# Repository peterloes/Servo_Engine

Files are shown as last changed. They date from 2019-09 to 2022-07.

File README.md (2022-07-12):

# SERVO Engine

A standalone platform for animal manipulation. 

This is the firmware for project Servo_2015, a small board which allows to
control a servo via its PWM input. Setup and control of the servo is done
via 3 keys, and, for selecting the two end positions, also via two external
inputs, please see below. The firmware supports soft-start, i.e. the servo
speed will be ramped-up during the start phase.

Technical specifications:
- Input voltage: 12-42V
- Standby current consumption: 3mA@12V
- Maximum current consuption: 1.5A
- Dimensions: 60 × 50 × 10 mm

Supported:
- HiTEC HS-5646WP
- HiTEC HS 785(sailing winds)

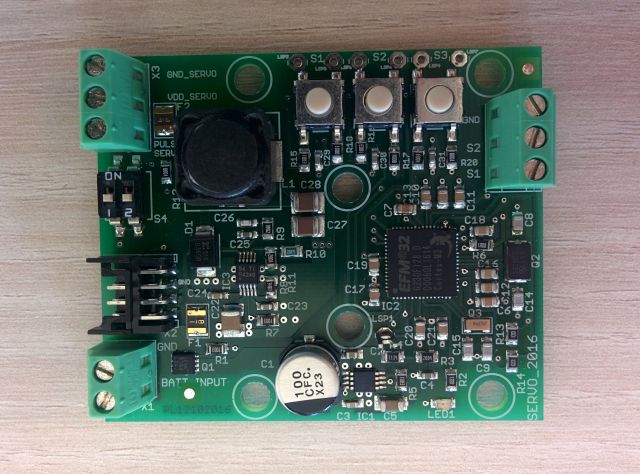
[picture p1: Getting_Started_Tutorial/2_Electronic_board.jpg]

 
 Setup Mode
 
 The servo setup procedure consists of 4 steps:
 - Adjust end position 1.  This can be the most left or the most right end
   point.  This position will be reached after power-up if valid servo data
   has been found in FLASH.
 - Adjust end position 2.  This is the opposite end position to position 1.
 - Adjust servo speed.  The servo permanently moves between the two end
   points.  The speed can be adjusted via S1 and S2.
 - Asserting S3 the 4th time stores the servo parameters into FLASH and
   returns to normal operation

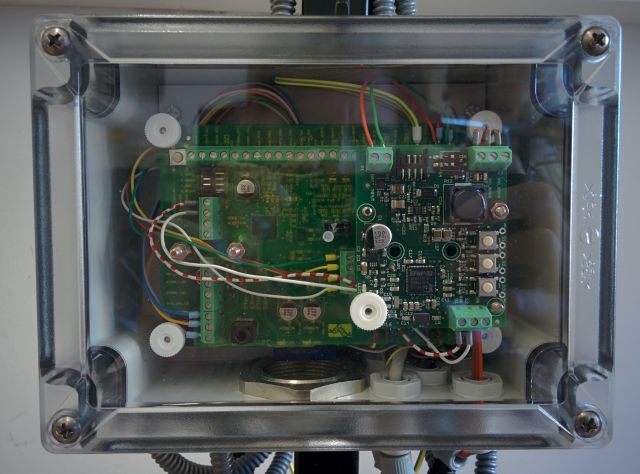
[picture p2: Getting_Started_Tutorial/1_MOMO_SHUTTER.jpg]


Bird Feeder Application (MOMO)

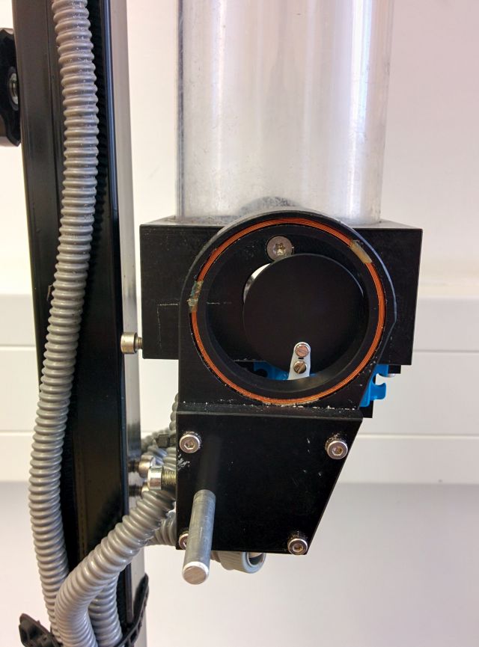
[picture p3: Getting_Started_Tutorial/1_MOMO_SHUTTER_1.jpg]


Bird Feeder Application

https://github.com/peterloes/Servo_Engine/blob/master/Getting_Started_Tutorial/1_poster_overview.pdf

Mainboard: 

https://github.com/peterloes/MOMO

https://github.com/peterloes/TAMDL

Manufacture:

https://github.com/peterloes/Servo_Engine/blob/master/Getting_Started_Tutorial/3_Supplier.txt

EXTENSIONS:

Electrical applications for non-deadly animal traps.

https://github.com/peterloes/SmartAnimalTraps

Antenna (horizontal) rotation over 360 degrees (HiTEC HS 785//sailing winds; 12V@25mA).

https://github.com/peterloes/Servo_Engine/blob/master/Getting_Started_Tutorial/2_Servo_Antenna_3turns.jpg (New firmware is not uploaded.)

Actuator for linear movements.

https://github.com/peterloes/Linear_Engine

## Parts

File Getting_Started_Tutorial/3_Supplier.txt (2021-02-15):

Supplier of all Electronic Boards

Top-Print Electronic GmbH
Oskar Schmid

Rosenheimer Landstr. 129a
85521 Ottobrunn
Germany
Tel.: +49-89-60668047
Fax: +49-89-60668049
mailto: info@top-print.eu
https://www.leiterplatten-muenchen.de/

Protective coating with Schmelzharz Bectron MR3404

KC – Kunststoff- Chemische Produkte GmbH
Holger Sarau-Burghardt

Leonberger Straße 86 
DE 71292 Friolzheim
phone: +49 (0)7044 9425 13
e-mail: h.sarau-burghardt@kc-produkte.com
http: www.conformalcoating.de

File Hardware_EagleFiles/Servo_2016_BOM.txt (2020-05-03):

Stückliste exportiert am 15.05.2018 12:53

Part  Value                Device                  Package                Description                                                    MF MPN OC_FARNELL OC_NEWARK
C1    100µ/16V             CPOL-EUE                PANASONIC_E            POLARIZED CAPACITOR, European symbol                                                      
C2    1uF                  C-EUC0603               C0603                  CAPACITOR, European symbol                                                                
C3    1nF                  C-EUC0603               C0603                  CAPACITOR, European symbol                                                                
C4    10nF                 C-EUC0603               C0603                  CAPACITOR, European symbol                                                                
C5    10uF                 C-EUC1206               C1206                  CAPACITOR, European symbol                                                                
C6    100n                 C_SMD0805               0805                                                                                                             
C7    1u                   C_SMD0805               0805                                                                                                             
C8    12p                  C_SMD0805               0805                                                                                                             
C9    18p                  C_SMD0805               0805                                                                                                             
C10   100n                 C_SMD0805               0805                                                                                                             
C11   100n                 C_SMD0805               0805                                                                                                             
C12   100n                 C_SMD0805               0805                                                                                                             
C13   100n                 C_SMD0805               0805                                                                                                             
C14   12p                  C_SMD0805               0805                                                                                                             
C15   18p                  C_SMD0805               0805                                                                                                             
C16   100n                 C_SMD0805               0805                                                                                                             
C17   100n                 C_SMD0805               0805                                                                                                             
C18   100n                 C_SMD0805               0805                                                                                                             
C19   100n                 C_SMD0805               0805                                                                                                             
C20   100n                 C_SMD0805               0805                                                                                                             
C21   100n                 C_SMD0805               0805                                                                                                             
C22   4.7µF                C-EUC1210               C1210                  CAPACITOR, European symbol                                                                
C23   10nF                 C-EUC0603               C0603                  CAPACITOR, European symbol                                                                
C24   100nF                C-EUC0603               C0603                  CAPACITOR, European symbol                                                                
C25   4.3nF                C-EUC0603               C0603                  CAPACITOR, European symbol                                                                
C26   24pF                 C-EUC0603               C0603                  CAPACITOR, European symbol                                                                
C27   22µF                 C-EUC1210               C1210                  CAPACITOR, European symbol                                                                
C28   22µF                 C-EUC1210               C1210                  CAPACITOR, European symbol                                                                
C29   10n                  C-EUC0603               C0603                  CAPACITOR, European symbol                                                                
C30   10n                  C-EUC0603               C0603                  CAPACITOR, European symbol                                                                
C31   10n                  C-EUC0603               C0603                  CAPACITOR, European symbol                                                                
D1    B360B                SCHOTTKY-DIODESMD       SMB                    Schottky Diode                                                                            
F1    USMF150              PFUF                    PFUF_1210POLY                                                                                                    
F2    USMF110              PFUF                    PFUF_1210POLY                                                                                                    
IC1   TPS7A1601DGNT        TPS7A16                 DGN_S-PDSO-G8-EXP                                                                                                
IC2   EFM32G230F128        EFM32G230F128           QFN64                  EFM32G230F128 Gecko Microcontroller in 9mm x 9mm QFN64 package                            
IC3   TPS54240DGQR         TPS54240DGQR            S-PDSO-G10                                                                                                       
L1    PIS4728-220M-04      DR127                   DR127                  High Power Density, High Efficiency, Shielded Inductors                                   
LED1  SML-H12U8TT86        LEDCHIPLED_0805         CHIPLED_0805           LED                                                                                       
LSP1  (n.b.)LSP10          LSP10                   LSP10                  SOLDER PAD drill 1.0 mm, distributor Buerklin, 12H555                                     
LSP2  (n.b.)LSP10          LSP10                   LSP10                  SOLDER PAD drill 1.0 mm, distributor Buerklin, 12H555                                     
LSP3  (n.b.)LSP10          LSP10                   LSP10                  SOLDER PAD drill 1.0 mm, distributor Buerklin, 12H555                                     
LSP4  (n.b.)LSP10          LSP10                   LSP10                  SOLDER PAD drill 1.0 mm, distributor Buerklin, 12H555                                     
LSP5  (n.b.)LSP10          LSP10                   LSP10                  SOLDER PAD drill 1.0 mm, distributor Buerklin, 12H555                                     
LSP6  (n.b.)LSP10          LSP10                   LSP10                  SOLDER PAD drill 1.0 mm, distributor Buerklin, 12H555                                     
LSP7  (n.b.)LSP10          LSP10                   LSP10                  SOLDER PAD drill 1.0 mm, distributor Buerklin, 12H555                                     
PASS1 ROUND_1MM1.5         ROUND_1MM1.5            ROUND2_1.5MM                                                                                                     
PASS2 ROUND_1MM1.5         ROUND_1MM1.5            ROUND2_1.5MM                                                                                                     
Q1    SI7121DN             TRANSISTOR-FET_SI7113DN TRANSISTOR-FET_1212-8S                                                                                           
Q2    NX5032GA/32MHz/8pF   CRYSTAL2P5.0X3.2        CRYSTAL2P5.0X3.2       Quarz Crystal                                                                             
Q3    CM7V, 32768Hz/12.5pF CRYSTAL2P               CRYSTAL2P3.2X1.5       Quarz Crystal                                                                             
R1    100k                 R-EU_R0805              R0805                  RESISTOR, European symbol                                                                 
R2    1K2                  R-EU_R0805              R0805                  RESISTOR, European symbol                                                                 
R3    2M                   R-EU_R0805              R0805                  RESISTOR, European symbol                                                                 
R4    1M13                 R-EU_R0805              R0805                  RESISTOR, European symbol                                                                 
R5    100K                 R-EU_R0805              R0805                  RESISTOR, European symbol                                                                 
R6    1                    R-EU_R0805              R0805                  RESISTOR, European symbol                                                                 
R7    100K                 R-EU_R0805              R0805                  RESISTOR, European symbol                                                                 
R8    348K                 R-EU_R0805              R0805                  RESISTOR, European symbol                                                                 
R9    39K                  R-EU_R0805              R0805                  RESISTOR, European symbol                                                                 
R10   53K                  R-EU_R0805              R0805                  RESISTOR, European symbol                                                                 
R11   10k                  R-EU_R0805              R0805                  RESISTOR, European symbol                                                                 
R12   100                  R-EU_R0805              R0805                  RESISTOR, European symbol                                                                 
R13   1K                   R-EU_R0805              R0805                  RESISTOR, European symbol                                                                 
R14   1K                   R-EU_R0805              R0805                  RESISTOR, European symbol                                                                 
R15   100K                 R-EU_R0805              R0805                  RESISTOR, European symbol                                                                 
R16   100K                 R-EU_R0805              R0805                  RESISTOR, European symbol                                                                 
R17   100K                 R-EU_R0805              R0805                  RESISTOR, European symbol                                                                 
R18   100                  R-EU_R0805              R0805                  RESISTOR, European symbol                                                                 
R19   100                  R-EU_R0805              R0805                  RESISTOR, European symbol                                                                 
R20   100                  R-EU_R0805              R0805                  RESISTOR, European symbol                                                                 
S1    SWPB_B3S1000         DTSM-6                  DTSM-6                                                                                                           
S2    SWPB_B3S1000         DTSM-6                  DTSM-6                                                                                                           
S3    SWPB_B3S1000         DTSM-6                  DTSM-6                                                                                                           
S4    SBS9102TK            219-02                  CTS-219-02             Surface Mount DIP Switch Series 219 SMT                               unknown    unknown  
X1    MKDS1/2-3,81         MKDS1/2-3,81            2POL381                MKDS 1/2-3,81 - Order No. 1727010 (RS-Online - 101-5384)                                  
X2    DP11_8DP_2DS         DP11_8DP_2DS            DP11_8DP-2DS                                                                                                     
X3    MKDS1/3-3,81         MKDS1/3-3,81            3POL381                MKDS 1/3-3,81 - Order No. 1727023 (RS-Online - 101-5390)                                  
X4    MKDS1/3-3,81         MKDS1/3-3,81            3POL381                MKDS 1/3-3,81 - Order No. 1727023 (RS-Online - 101-5390)

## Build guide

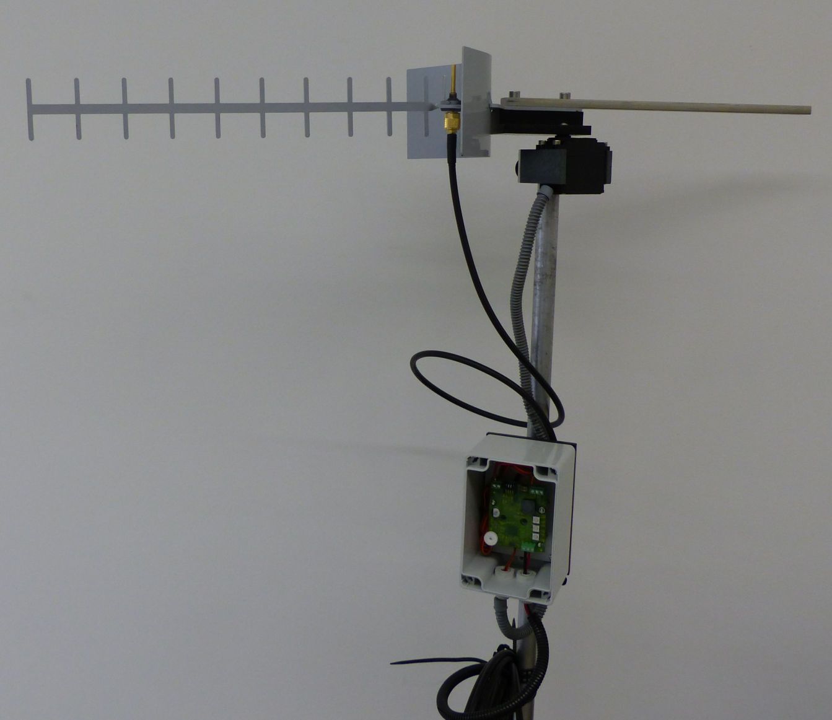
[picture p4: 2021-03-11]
Getting_Started_Tutorial/4_Servo_Antenna_3turns.JPG

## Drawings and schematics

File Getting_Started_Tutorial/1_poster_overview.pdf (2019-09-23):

## Multifunctional Mainboard to Observe and Manipulate Organisms (MOMO) RFID Readers and SERVO Engines

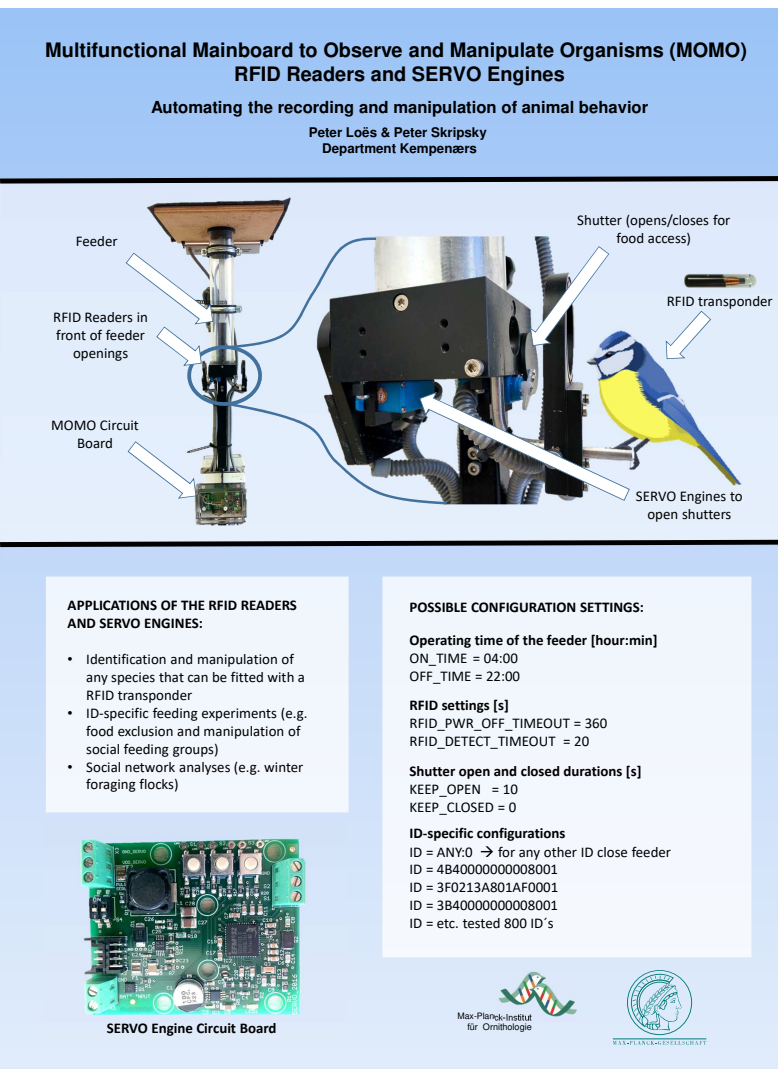
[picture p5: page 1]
APPLICATIONS OF THE RFID READERS; POSSIBLE CONFIGURATION SETTINGS:; Feeder; RFID transponder; RFID settings [s] RFID_PWR_OFF_TIMEOUT = 360 RFID_DETECT_TIMEOUT = 20; MOMO Circuit Board

Automating the recording and manipulation of animal behavior

Peter Loës & Peter Skripsky
Department Kempenærs

Shutter (opens/closes for
food access)

RFID Readers in
front of feeder
openings

SERVO Engines to
open shutters

AND SERVO ENGINES:

Operating time of the feeder [hour:min]
ON_TIME = 04:00
OFF_TIME = 22:00

• Identification and manipulation of
any species that can be fitted with a
RFID transponder
• ID-specific feeding experiments (e.g.
food exclusion and manipulation of
social feeding groups)
• Social network analyses (e.g. winter
foraging flocks)

Shutter open and closed durations [s]
KEEP_OPEN = 10
KEEP_CLOSED = 0

ID-specific configurations
ID = ANY:0 → for any other ID close feeder
ID = etc. tested 800 ID´s

Max-Planck-Institut
für Ornithologie

SERVO Engine Circuit Board

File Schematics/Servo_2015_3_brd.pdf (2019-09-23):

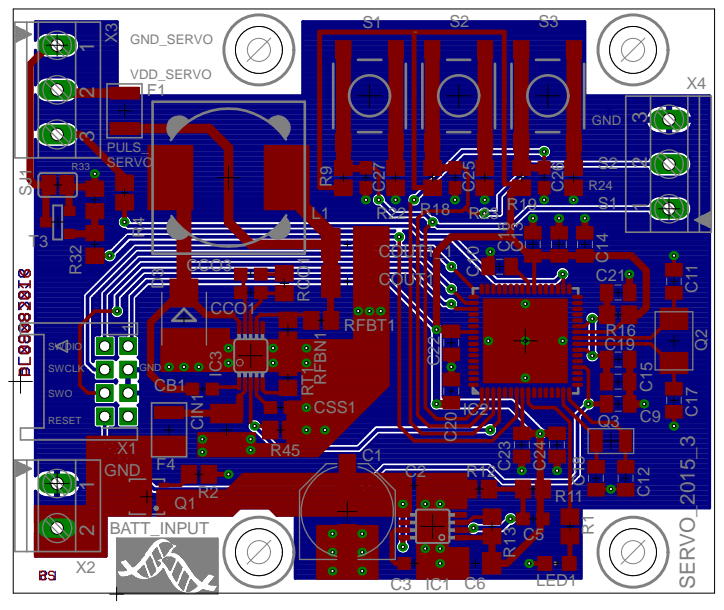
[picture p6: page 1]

SERVO | S2

RFBT1

R16
C19

SWDIO

SWO

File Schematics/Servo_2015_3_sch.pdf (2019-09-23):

## Wide Input Voltage Range: 12V to 42V VDD_SERVO 5V benötigt max. VIN 8V

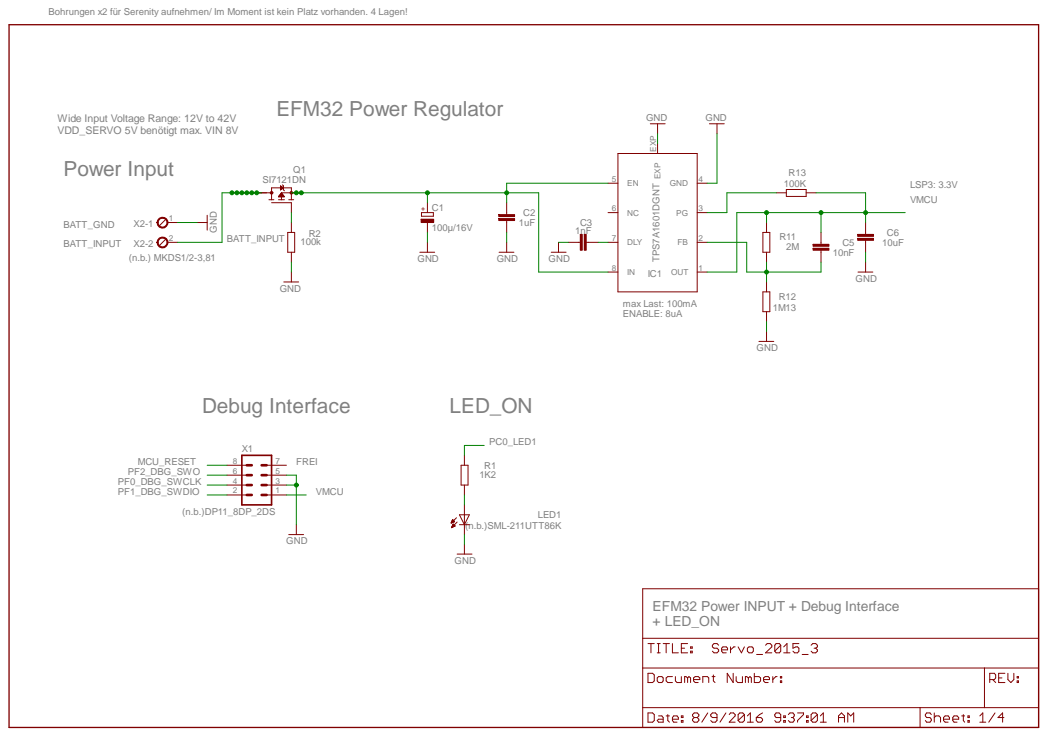
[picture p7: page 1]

Bohrungen x2 für Serenity aufnehmen/ Im Moment ist kein Platz vorhanden. 4 Lagen!

EFM32 Power INPUT + Debug Interface
+ LED_ON

# EFM32 I/O + POWER

# CL f. 32KHz crystal = 22pF as in STK3600

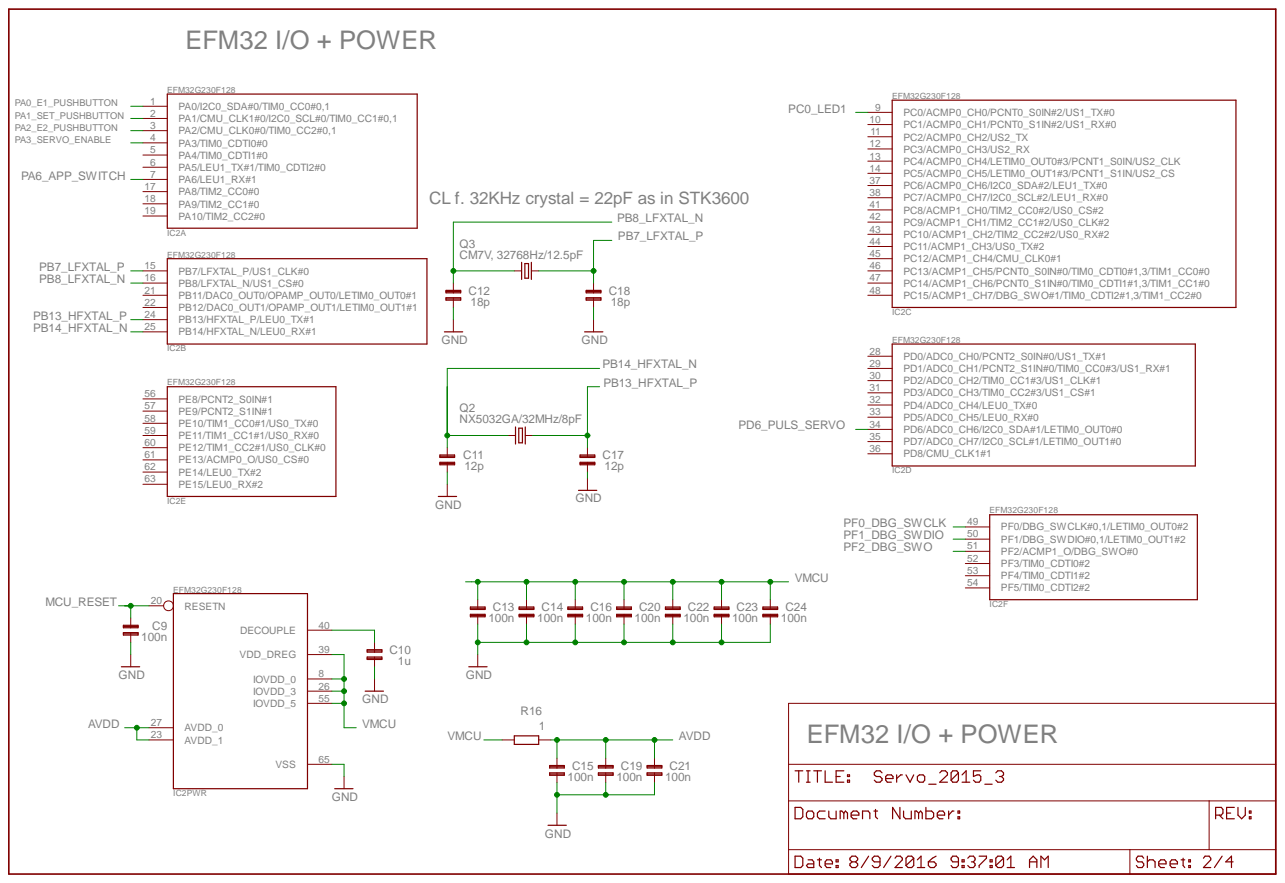
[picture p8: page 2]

# 5V_Ausgabe

# POWER OUTPUTs

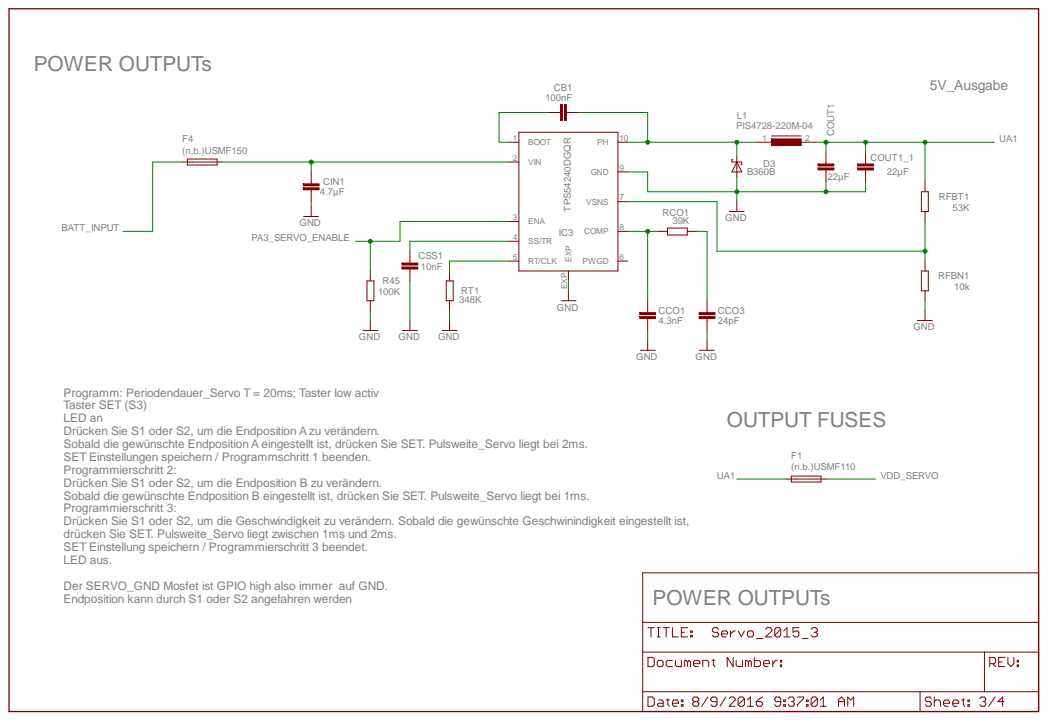
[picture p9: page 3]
POWER OUTPUTs; OUTPUT FUSES; GND; TPS54240DGQR; PIS4728-220M-04; (n.b.)USMF150; (n.b.)USMF110; CCO3; CSS1; RCO1; CIN1; VIN 2; ENA 3; VSNS; BOOT 1; COMP; RT/CLK 5; EXP EXP; PWGD; CCO1; RFBT1; RFBN1; COUT1; COUT1_1; VDD_SERVO; PA3_SERVO_ENABLE; BATT_INPUT

Programm: Periodendauer_Servo T = 20ms; Taster low activ
Taster SET (S3)
LED an
Drücken Sie S1 oder S2, um die Endposition A zu verändern.
Sobald die gewünschte Endposition A eingestellt ist, drücken Sie SET. Pulsweite_Servo liegt bei 2ms.
SET Einstellungen speichern / Programmschritt 1 beenden.
Programmierschritt 2:
Drücken Sie S1 oder S2, um die Endposition B zu verändern.
Sobald die gewünschte Endposition B eingestellt ist, drücken Sie SET. Pulsweite_Servo liegt bei 1ms.
Programmierschritt 3:
Drücken Sie S1 oder S2, um die Geschwindigkeit zu verändern. Sobald die gewünschte Geschwinindigkeit eingestellt ist,
drücken Sie SET. Pulsweite_Servo liegt zwischen 1ms und 2ms.
SET Einstellung speichern / Programmierschritt 3 beendet.
LED aus.

Der SERVO_GND Mosfet ist GPIO high also immer auf GND.
Endposition kann durch S1 oder S2 angefahren werden

# SERVO

## HITEC, C131_Graupner:

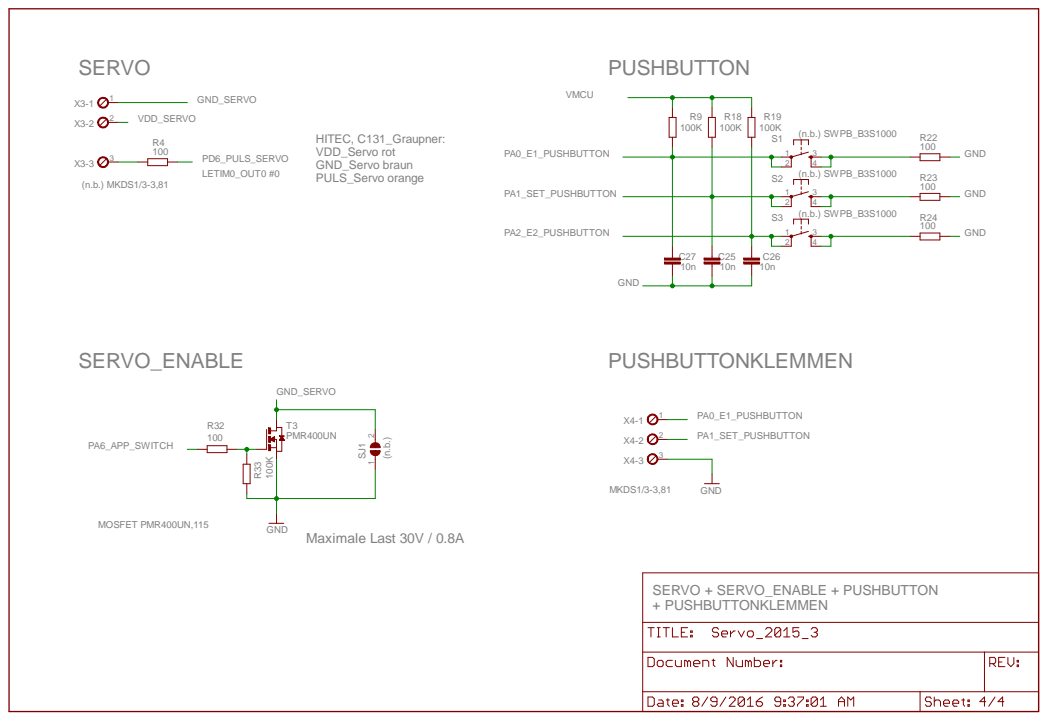
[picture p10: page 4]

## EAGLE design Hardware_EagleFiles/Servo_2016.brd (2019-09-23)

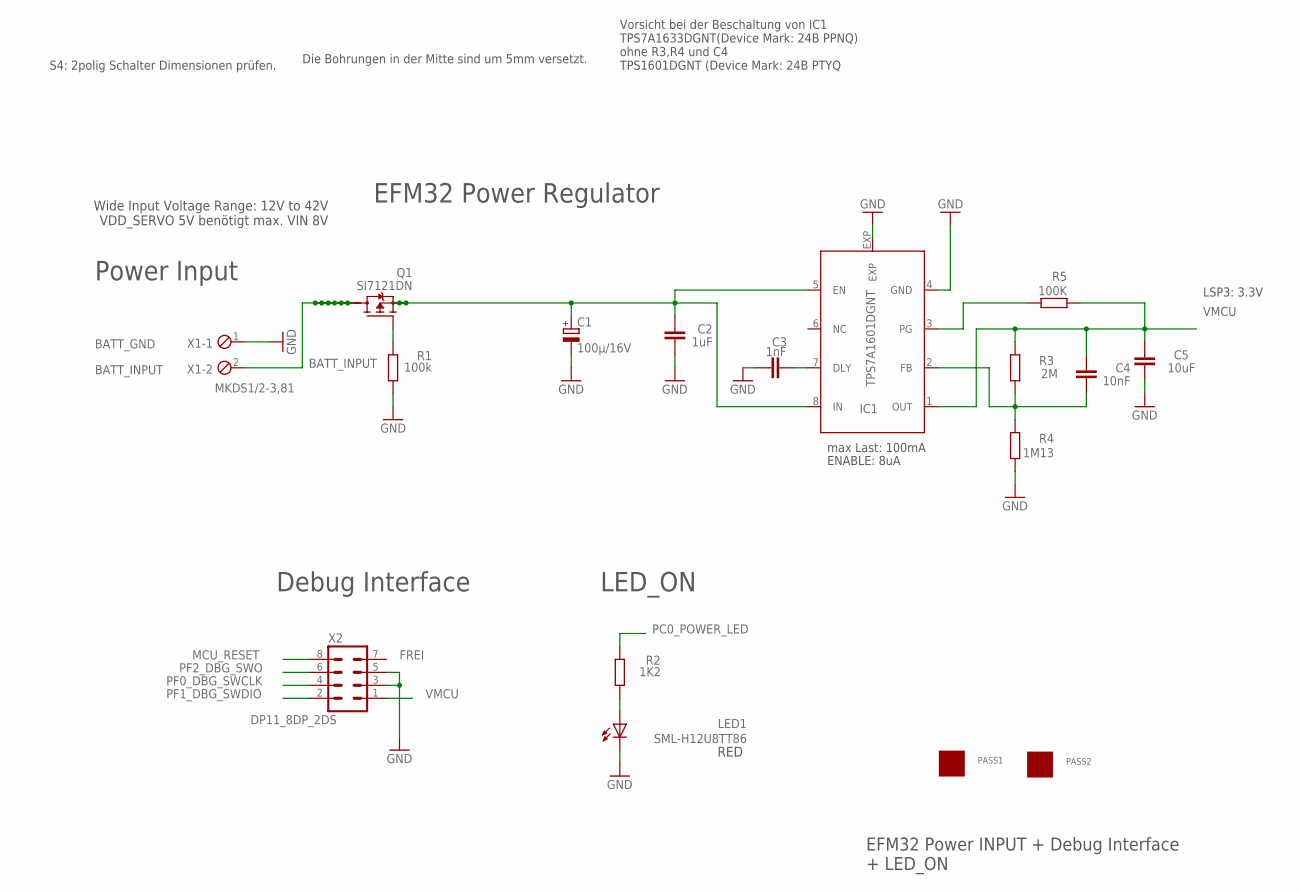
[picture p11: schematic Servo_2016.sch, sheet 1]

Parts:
C1: 100µ/16V; PANASONIC_E
C2: 1uF; C0603
C3: 1nF; C0603
C4: 10nF; C0603
C5: 10uF; C1206
IC1: TPS7A1601DGNT; DGN_S-PDSO-G8-EXP
LED1: SML-H12U8TT86; CHIPLED_0805
PASS1, PASS2: ROUND_1MM1.5; ROUND2_1.5MM
Q1: SI7121DN; TRANSISTOR-FET_1212-8S
R1: 100k; R0805
R2: 1K2; R0805
R3: 2M; R0805
R4: 1M13; R0805
R5: 100K; R0805
X1: MKDS1/2-3,81; 2POL381
X2: DP11_8DP_2DS; DP11_8DP-2DS

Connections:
BATT_INPUT: Q1.5 (D), Q1.6 (D), Q1.7 (D), Q1.8 (D), Q1.9 (D), Q1.10 (D), Q1.11 (D), X1.2; also elsewhere on the board
GND: C1.-, C2.1, C3.1, C5.1, IC1.4 (GND), IC1.EXP, LED1.C, R1.1, R4.1, X1.1, X2.3, X2.5; also elsewhere on the board
MCU_RESET: X2.8; also elsewhere on the board
unnamed: C1.+, C2.2, IC1.5 (EN), IC1.8 (IN), Q1.1 (S), Q1.2 (S), Q1.3 (S)
unnamed: C3.2, IC1.7 (DLY)
unnamed: C4.1, IC1.2 (FB), R3.1, R4.2
unnamed: IC1.3 (PG), R5.2
unnamed: Q1.4 (G), R1.2
unnamed: LED1.A, R2.2
PC0_POWER_LED: R2.1; also elsewhere on the board
PF0_DBG_SWCLK: X2.4; also elsewhere on the board
PF1_DBG_SWDIO: X2.2; also elsewhere on the board
PF2_DBG_SWO: X2.6; also elsewhere on the board
VMCU: C4.2, C5.2, IC1.1 (OUT), R3.2, R5.1, X2.1; also elsewhere on the board

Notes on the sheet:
BATT_GND
Wide Input Voltage Range: 12V to 42V VDD_SERVO 5V benötigt max. VIN 8V
BATT_INPUT
EFM32 Power INPUT + Debug Interface + LED_ON
ENABLE: 8uA
Power Input
max Last: 100mA
LSP3: 3.3V
EFM32 Power Regulator
Debug Interface
LED_ON
FREI
Vorsicht bei der Beschaltung von IC1 TPS7A1633DGNT(Device Mark: 24B PPNQ) ohne R3,R4 und C4 TPS1601DGNT (Device Mark: 24B PTYQ
S4: 2polig Schalter Dimensionen prüfen.
Die Bohrungen in der Mitte sind um 5mm versetzt.
RED

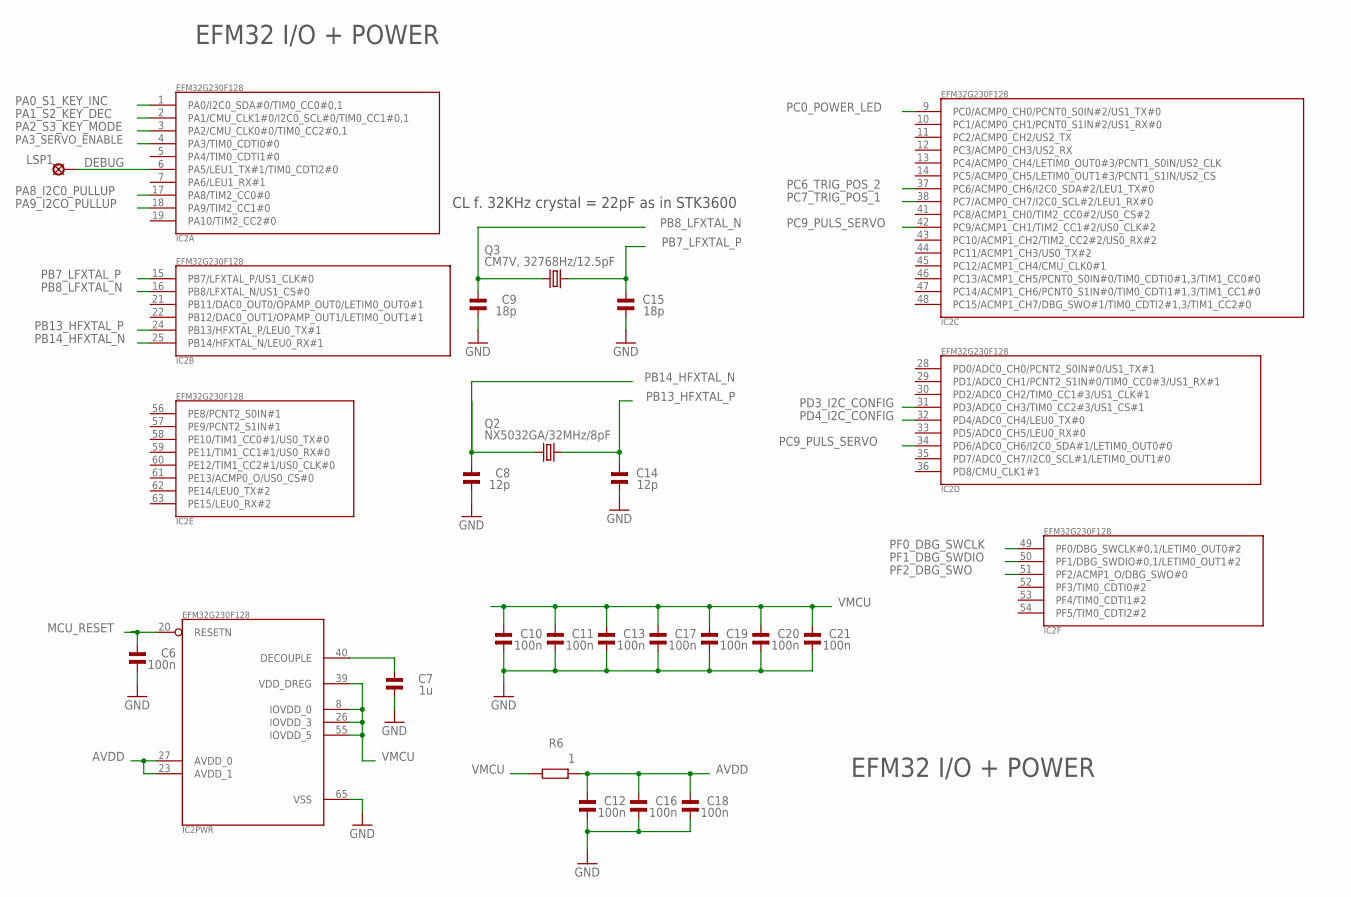
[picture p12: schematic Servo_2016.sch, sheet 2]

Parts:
C6, C10, C11, C12, C13, C16, C17, C18, C19, C20, C21: 100n; 0805
C7: 1u; 0805
C8, C14: 12p; 0805
C9, C15: 18p; 0805
IC2: EFM32G230F128; QFN64
LSP1: (n.b.)LSP10; LSP10
Q2: NX5032GA/32MHz/8pF; CRYSTAL2P5.0X3.2
Q3: CM7V, 32768Hz/12.5pF; CRYSTAL2P3.2X1.5
R6: 1; R0805

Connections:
AVDD: C12.2, C16.2, C18.2, IC2.23 (AVDD_1), IC2.27 (AVDD_0), R6.2
DEBUG: IC2.6 (PA5/LEU1_TX#1/TIM0_CDTI2#0), LSP1.MP
GND: C6.1, C7.1, C8.1, C9.1, C10.1, C11.1, C12.1, C13.1, C14.1, C15.1, C16.1, C17.1, C18.1, C19.1, C20.1, C21.1, IC2.65 (VSS); also elsewhere on the board
MCU_RESET: C6.2, IC2.20 (RESETN); also elsewhere on the board
unnamed: C7.2, IC2.40 (DECOUPLE)
PA0_S1_KEY_INC: IC2.1 (PA0/I2C0_SDA#0/TIM0_CC0#0,1); also elsewhere on the board
PA1_S2_KEY_DEC: IC2.2 (PA1/CMU_CLK1#0/I2C0_SCL#0/TIM0_CC1#0,1); also elsewhere on the board
PA2_S3_KEY_MODE: IC2.3 (PA2/CMU_CLK0#0/TIM0_CC2#0,1); also elsewhere on the board
PA3_SERVO_ENABLE: IC2.4 (PA3/TIM0_CDTI0#0); also elsewhere on the board
PA8_I2C0_PULLUP: IC2.17 (PA8/TIM2_CC0#0); also elsewhere on the board
PA9_I2CO_PULLUP: IC2.18 (PA9/TIM2_CC1#0); also elsewhere on the board
PB7_LFXTAL_P: C15.2, IC2.15 (PB7/LFXTAL_P/US1_CLK#0), Q3.2
PB8_LFXTAL_N: C9.2, IC2.16 (PB8/LFXTAL_N/US1_CS#0), Q3.1
PB13_HFXTAL_P: C14.2, IC2.24 (PB13/HFXTAL_P/LEU0_TX#1), Q2.2
PB14_HFXTAL_N: C8.2, IC2.25 (PB14/HFXTAL_N/LEU0_RX#1), Q2.1
PC0_POWER_LED: IC2.9 (PC0/ACMP0_CH0/PCNT0_S0IN#2/US1_TX#0); also elsewhere on the board
PC6_TRIG_POS_2: IC2.37 (PC6/ACMP0_CH6/I2C0_SDA#2/LEU1_TX#0); also elsewhere on the board
PC7_TRIG_POS_1: IC2.38 (PC7/ACMP0_CH7/I2C0_SCL#2/LEU1_RX#0); also elsewhere on the board
PC9_PULS_SERVO: IC2.34 (PD6/ADC0_CH6/I2C0_SDA#1/LETIM0_OUT0#0), IC2.42 (PC9/ACMP1_CH1/TIM2_CC1#2/US0_CLK#2); also elsewhere on the board
PD3_I2C_CONFIG: IC2.31 (PD3/ADC0_CH3/TIM0_CC2#3/US1_CS#1); also elsewhere on the board
PD4_I2C_CONFIG: IC2.32 (PD4/ADC0_CH4/LEU0_TX#0); also elsewhere on the board
PF0_DBG_SWCLK: IC2.49 (PF0/DBG_SWCLK#0,1/LETIM0_OUT0#2); also elsewhere on the board
PF1_DBG_SWDIO: IC2.50 (PF1/DBG_SWDIO#0,1/LETIM0_OUT1#2); also elsewhere on the board
PF2_DBG_SWO: IC2.51 (PF2/ACMP1_O/DBG_SWO#0); also elsewhere on the board
VMCU: C10.2, C11.2, C13.2, C17.2, C19.2, C20.2, C21.2, IC2.8 (IOVDD_0), IC2.26 (IOVDD_3), IC2.39 (VDD_DREG), IC2.55 (IOVDD_5), R6.1; also elsewhere on the board

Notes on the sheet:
EFM32 I/O + POWER
CL f. 32KHz crystal = 22pF as in STK3600

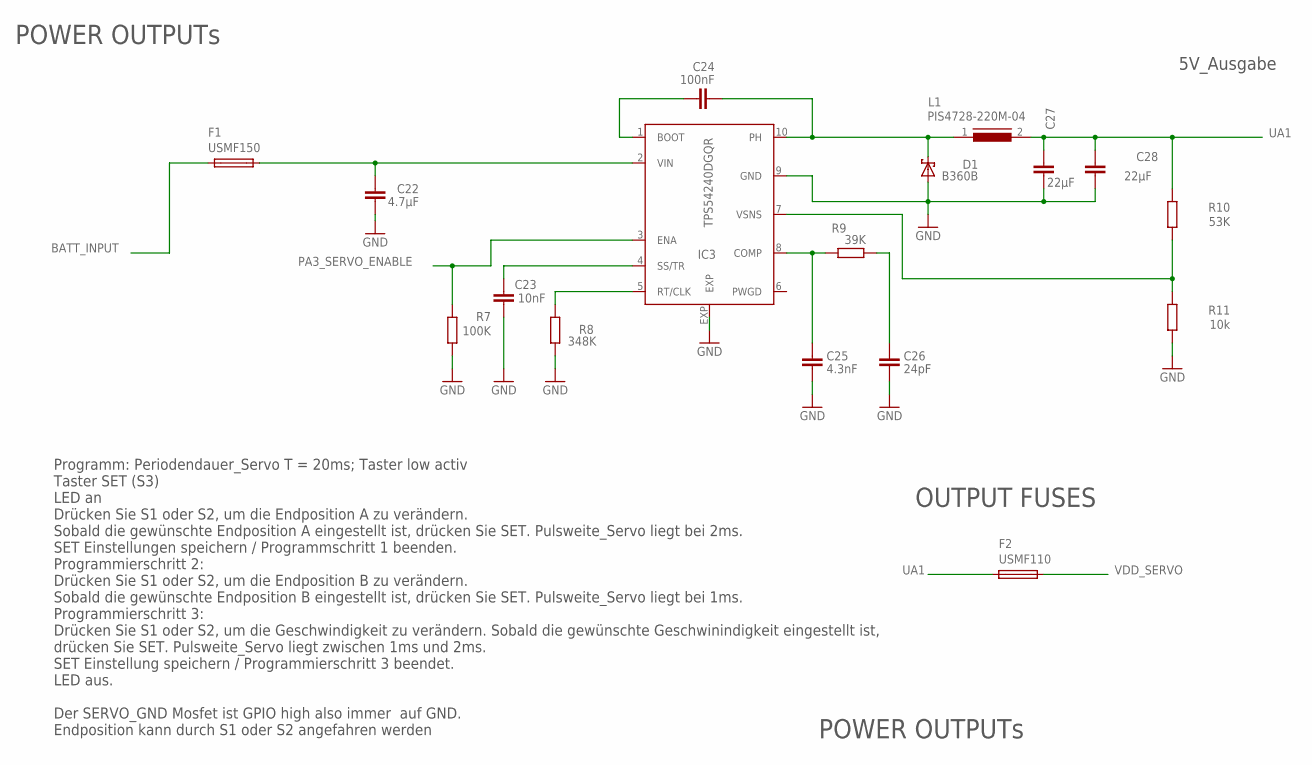
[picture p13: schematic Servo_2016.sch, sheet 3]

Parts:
C22: 4.7µF; C1210
C23: 10nF; C0603
C24: 100nF; C0603
C25: 4.3nF; C0603
C26: 24pF; C0603
C27, C28: 22µF; C1210
D1: B360B; SMB
F1: USMF150; PFUF_1210POLY
F2: USMF110; PFUF_1210POLY
IC3: TPS54240DGQR; S-PDSO-G10
L1: PIS4728-220M-04; DR127
R7: 100K; R0805
R8: 348K; R0805
R9: 39K; R0805
R10: 53K; R0805
R11: 10k; R0805

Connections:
BATT_INPUT: F1.P$1 (1); also elsewhere on the board
GND: C22.2, C23.2, C25.2, C26.2, C27.2, C28.2, D1.A, IC3.9 (GND), IC3.EXP, R7.1, R8.1, R11.1; also elsewhere on the board
unnamed: IC3.5 (RT/CLK), R8.2
unnamed: C24.2, IC3.1 (BOOT)
unnamed: C24.1, D1.C, IC3.10 (PH), L1.1
unnamed: C23.1, IC3.4 (SS/TR)
unnamed: C25.1, IC3.8 (COMP), R9.1
unnamed: C26.1, R9.2
unnamed: IC3.7 (VSNS), R10.1, R11.2
unnamed: C22.1, F1.P$2 (2), IC3.2 (VIN)
PA3_SERVO_ENABLE: IC3.3 (ENA), R7.2; also elsewhere on the board
UA1: C27.1, C28.1, F2.P$1 (1), L1.2, R10.2
VDD_SERVO: F2.P$2 (2); also elsewhere on the board

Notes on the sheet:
5V_Ausgabe
POWER OUTPUTs
OUTPUT FUSES
Programm: Periodendauer_Servo T = 20ms; Taster low activ Taster SET (S3) LED an Drücken Sie S1 oder S2, um die Endposition A zu verändern. Sobald die gewünschte Endposition A eingestellt ist, drücken Sie SET. Pulsweite_Servo liegt bei 2ms. SET Einstellungen speichern / Programmschritt 1 beenden. Pr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

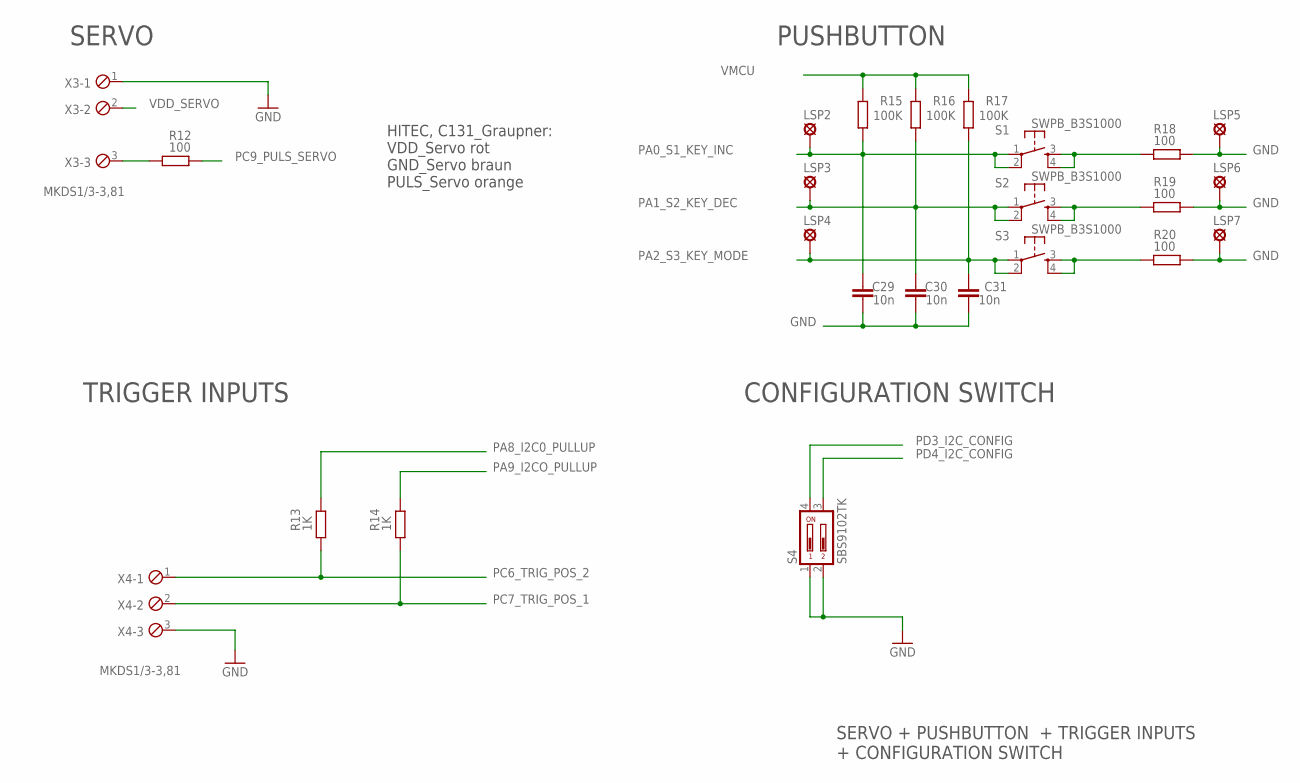
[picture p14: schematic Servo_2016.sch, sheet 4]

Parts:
C29, C30, C31: 10n; C0603
LSP2, LSP3, LSP4, LSP5, LSP6, LSP7: (n.b.)LSP10; LSP10
R12, R18, R19, R20: 100; R0805
R13, R14: 1K; R0805
R15, R16, R17: 100K; R0805
S1, S2, S3: SWPB_B3S1000; DTSM-6
S4: SBS9102TK; CTS-219-02
X3, X4: MKDS1/3-3,81; 3POL381

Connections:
GND: C29.1, C30.1, C31.1, LSP5.MP, LSP6.MP, LSP7.MP, R18.2, R19.2, R20.2, S4.1, S4.2, X3.1, X4.3; also elsewhere on the board
unnamed: R12.1, X3.3
unnamed: R20.1, S3.3, S3.4
unnamed: R18.1, S1.3, S1.4
unnamed: R19.1, S2.3, S2.4
PA0_S1_KEY_INC: C29.2, LSP2.MP, R15.1, S1.1, S1.2; also elsewhere on the board
PA1_S2_KEY_DEC: C30.2, LSP3.MP, R16.1, S2.1, S2.2; also elsewhere on the board
PA2_S3_KEY_MODE: C31.2, LSP4.MP, R17.1, S3.1, S3.2; also elsewhere on the board
PA8_I2C0_PULLUP: R13.2; also elsewhere on the board
PA9_I2CO_PULLUP: R14.2; also elsewhere on the board
PC6_TRIG_POS_2: R13.1, X4.1; also elsewhere on the board
PC7_TRIG_POS_1: R14.1, X4.2; also elsewhere on the board
PC9_PULS_SERVO: R12.2; also elsewhere on the board
PD3_I2C_CONFIG: S4.4; also elsewhere on the board
PD4_I2C_CONFIG: S4.3; also elsewhere on the board
VDD_SERVO: X3.2; also elsewhere on the board
VMCU: R15.2, R16.2, R17.2; also elsewhere on the board

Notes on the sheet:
SERVO + PUSHBUTTON + TRIGGER INPUTS + CONFIGURATION SWITCH
SERVO
HITEC, C131_Graupner: VDD_Servo rot GND_Servo braun PULS_Servo orange
TRIGGER INPUTS
PUSHBUTTON
CONFIGURATION SWITCH

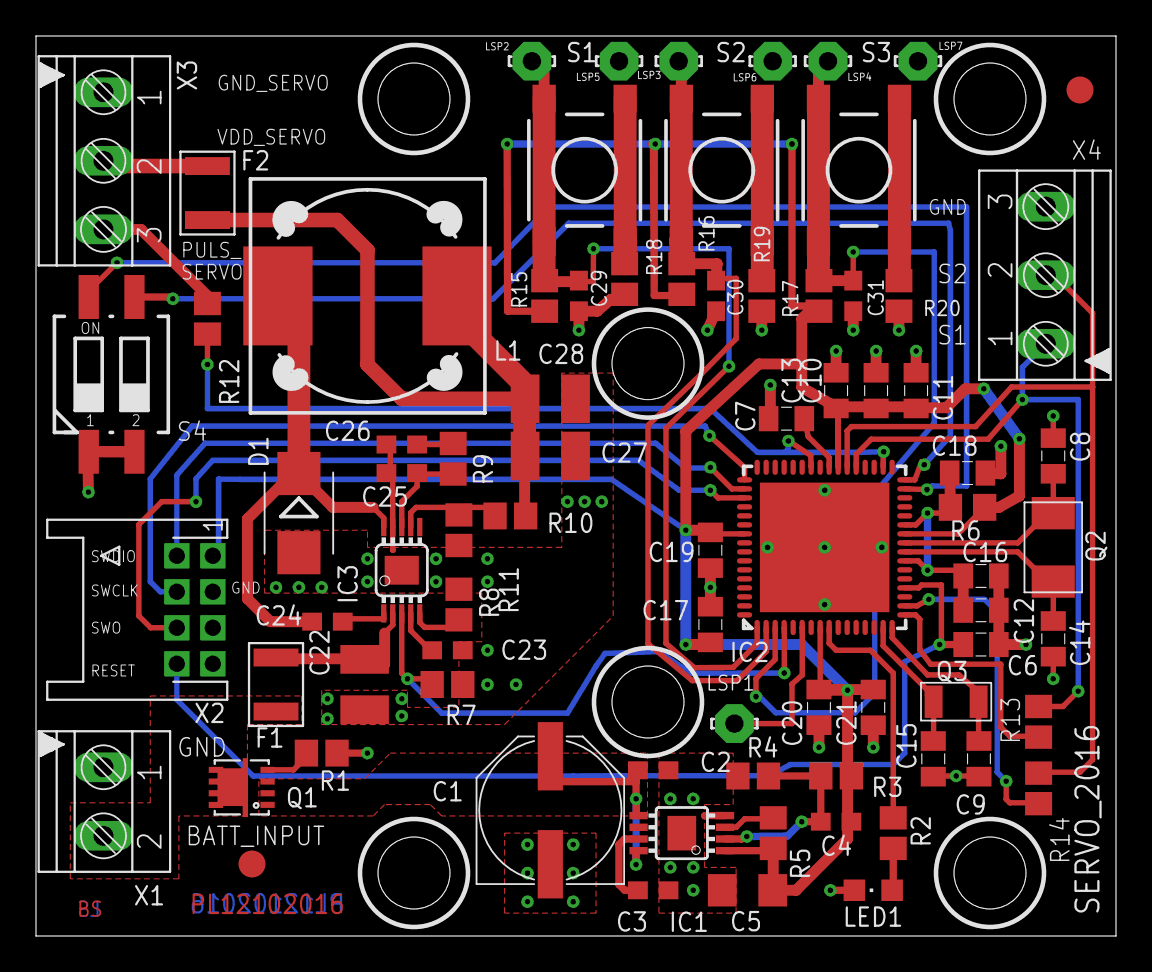
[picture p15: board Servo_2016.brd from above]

Board: 2 copper layers, 60.0 x 50.0 mm, 79 parts (0 on the bottom side), 46 nets.

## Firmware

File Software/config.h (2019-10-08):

/***************************************************************************//**
 * @file
 * @brief	Project configuration file
 * @author	Ralf Gerhauser
 * @version	2016-10-05
 *
 * This file allows to set miscellaneous configuration parameters.  It must be
 * included by all modules.
 *
 ****************************************************************************//*
Revision History:
2016-09-09,rage	Derived from project "SNB_Heaven".
*/

#ifndef __INC_config_h
#define __INC_config_h

/*=============================== Header Files ===============================*/

#include <stdio.h>
#include <stdbool.h>
#include "em_device.h"

/*=============================== Definitions ================================*/

/*
 * Basic defines - should all be moved to Generic.h
 */
    /* terminators for lists and strings */

#define	EOL		NULL		/* EndOfList		*/
#define EOS		'\0'		/* EndOfString		*/
#define	NONE		(-1)

    /* macro to calculate the number of elements of an array */
#define ELEM_CNT(array)  (sizeof (array) / sizeof ((array)[0]))

/*
 * Port numbers - used to select a dedicated configuration for SERVO_PORT_NUM
 *
 * Note: For the 64pin package there are no LETIMER0 outputs on port A and E.
 */
#define GPIO_PORT_B	1
#define GPIO_PORT_C	2
#define GPIO_PORT_D	3
#define GPIO_PORT_F	5

/*
 * LED Definitions for this project
 */
    /*!@brief GPIO Port of the (red) Power-LED. */
#define POWER_LED_PORT		gpioPortC
    /*!@brief GPIO Pin of the (red) Power-LED. */
#define POWER_LED_PIN		0
    /*! @brief Macro to set or clear the Power-LED */
#define POWER_LED   IO_Bit(GPIO->P[POWER_LED_PORT].DOUT, POWER_LED_PIN)

/*!
 * @brief MPU Clock Configuration.
 *
 * Set to 0 to use the internal RC oscillator, if 1 the external 32MHz XTAL
 * is used - must be set 1 for this project.
 */
#define USE_EXT_32MHZ_CLOCK	1

/*
 * Configuration for module "AlarmClock"
 */
    /*!@brief RTC frequency in [Hz]. */
#define RTC_COUNTS_PER_SEC	32768


/*================================== Macros ==================================*/

#ifdef DEBUG
    /*
     * Debugging output via ITM
     */
    #define DBG_PUTC(ch)	ITM_SendChar(ch)
    #define DBG_PUTS(str)	ITM_SendStr(str)
    uint32_t ITM_SendChar (uint32_t ch);
    void ITM_SendStr(const char *pStr);
    void dbgInit(void);
#else
    #define DBG_PUTC(ch)
    #define DBG_PUTS(str)
#endif

    /*! Macro to address a single bit in the I/O range (peripheral range) in
     *  an atomic manner.
     * @param address   I/O register address.
     * @param bitNum    Bit number within this register.
     */
#define IO_BIT_ADDR(address, bitNum)					\
	((__IO uint32_t *) (BITBAND_PER_BASE				\
			+ (((uint32_t)(address)) - PER_MEM_BASE) * 32	\
			+ (bitNum) * 4))

    /*! Shortcut to directly access an I/O-bit. */
#define IO_Bit(regName, bitNum)	*IO_BIT_ADDR(&regName, bitNum)

    /*! Macro to address a single bit in an SRAM variable in an atomic manner.
     * @param address   Address of the variable in SRAM.
     * @param bitNum    Bit number within this variable.
     */
#define SRAM_BIT_ADDR(address, bitNum)					\
	((__IO uint32_t *) (BITBAND_RAM_BASE				\
			+ (((uint32_t)(address)) - RAM_MEM_BASE) * 32	\
			+ (bitNum) * 4))

    /*! Shortcut to directly access a bit in a variable. */
#define Bit(varName, bitNum)	*SRAM_BIT_ADDR(&varName, bitNum)

/*=========================== Typedefs and Structs ===========================*/

/*!@brief Structure to hold Project Information */
typedef struct
{
    char const  ID[12];
    char const  Date[16];
    char const  Time[10];
    char const  Version[16];
} PRJ_INFO;


/*!@brief Enumeration of Alarm Identifiers
 *
 * This is the list of Alarm IDs used by this application.  They are used to
 * identify a particular alarm time entry via the <b>alarmNum</b> parameter
 * when calling alarm functions, e.g. AlarmSet().
 */
typedef enum
{
    END_ALARM_ID
} ALARM_ID;


/*!@brief Enumeration of the EM1 Modules
 *
 * This is the list of Software Modules that require EM1 to work, i.e. they
 * will not work in EM2 because clocks, etc. would be disabled.  These enums
 * are used to set/clear the appropriate bit in the @ref g_EM1_ModuleMask.
 */
typedef enum
{
    EM1_MOD_SERVO,	//!<  0: Servo timers require the 32MHz HF clock
    END_EM1_MODULES
} EM1_MODULES;

/*======================== External Data and Routines ========================*/

extern volatile bool	 g_flgIRQ;		// Flag: Interrupt occurred
extern volatile uint16_t g_EM1_ModuleMask;	// Modules that require EM1


#endif /* __INC_config_h */

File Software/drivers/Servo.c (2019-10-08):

/***************************************************************************//**
 * @file
 * @brief	Servo Control
 * @author	Ralf Gerhauser
 * @version	2016-10-05
 *
 * This module provides the functionality to control a servo.  In detail, this
 * includes:
 * - Initialization and configuration of the required devices.
 * - PWM signal generation to control the servo position.
 * - A setup routine to adjust the end-points and speed of the servo.
 * - EEPROM-like storage to save the configuration.
 *
 * The firmware supports soft-start, i.e. the servo speed will be ramped-up
 * during the start phase.
 *
 * @warning
 * There must be a stable PWM signal before powering the servo, otherwise
 * the servo will start moving to a wrong position.
 *
 ****************************************************************************//*
Revision History:
2016-10-05,rage	Completed version 1.0, added support for external inputs.
2016-09-09,rage	Initial version.
*/

/*=============================== Header Files ===============================*/

#include <stdio.h>
#include "AlarmClock.h"
#include "Servo.h"
#include "em_device.h"
#include "em_assert.h"
#include "em_cmu.h"
#include "em_int.h"
#include "em_prs.h"
#include "em_timer.h"
#include "eeprom_emulation.h"

/*=============================== Definitions ================================*/

/*!@brief Minimum and maximum servo speed, i.e. the step width per 20ms. */
#define SERVO_MIN_SPEED	1
#define SERVO_MAX_SPEED	256

/*!@brief Servo position (PWM value) where calibration starts. */
#define SERVO_START_POS	((SERVO_PWM_MIN_VALUE + SERVO_PWM_MAX_VALUE) / 2)

/*! Magic ID for EEPROM block */
#define MAGIC_ID	0x0815

/*=========================== Typedefs and Structs ===========================*/

/*!@brief Operating and Setup modes for the servo. */
typedef enum
{
    SERVO_MODE_OPERATIONAL,	//!< 0: Normal servo operating mode
    SERVO_MODE_SETUP_POS_1,	//!< 1: Setup mode: adjust first position
    SERVO_MODE_SETUP_POS_2,	//!< 2: Setup mode: adjust second position
    SERVO_MODE_SETUP_SPEED,	//!< 3: Setup mode: adjust speed
    END_SERVO_MODE		//!< End of servo mode definitions
} SERVO_MODE;

/*================================ Local Data ================================*/

    /*! Timer handle for key inactivity timer */
static TIM_HDL		l_thTimeout = NONE;

    /*! Flag shows if there are valid servo settings stored in flash. */
static volatile bool	l_ServoDataValid = false;

    /*! Actual servo mode */
static volatile SERVO_MODE l_ServoMode = SERVO_MODE_SETUP_POS_1;

    /*! Actual servo position (PWM value) */
static volatile int	l_ServoPos = SERVO_START_POS;

    /*! Servo end-position 1 */
static volatile int	l_ServoPos_1 = SERVO_START_POS;

    /*! Servo end-position 2 */
static volatile int	l_ServoPos_2 = SERVO_START_POS;

    /*! Servo speed, i.e. delta position per 20ms */
static volatile int	l_ServoSpeed = SERVO_PWM_DFLT_SPEED;

    /*! Servo direction during speed calibration mode */
static volatile bool	l_DirIncrease;

    /*! Servo enable flag: true means ON, false means OFF */
static volatile bool	l_ServoEnable;

    /*! Servo start time counter (soft start) when servo starts moving [%] */
static volatile int	l_ServoStartCnt;

    /*! Servo stopping time counter after position has been reached [20ms] */
static volatile int	l_ServoStopCnt = SERVO_STOPPING_TIME;

    /*! Define the non-volatile variables. */
static EE_Variable_TypeDef  magic, pos1, pos2, speed, chksum;


/*=========================== Forward Declarations ===========================*/

static void	ServoKeyTimeout (TIM_HDL hdl);
static void	ServoCtrlEnable(void);
static void	ServoCtrlDisable(void);
static bool	ReadServoParms(void);
static void	WriteServoParms(void);

/***************************************************************************//**
 *
 * @brief	Servo control initialization
 *
 * This routine must be called once to initialize all the devices required to
 * control a servo.  It also loads the servo configuration (end-points and
 * speed) from FLASH.
 *
 ******************************************************************************/
void	ServoInit (void)
{
#if 1	// RAGE: should be hardwired
    /* Always enable GND for the Servo via PA6_APP_SWITCH */
    GPIO_PinModeSet(gpioPortA, 6, gpioModePushPull, 1);
#endif
    /* PA3_SERVO_ENABLE, SERVO_VDD*/
    GPIO_PinModeSet(SERVO_ENABLE_PORT, SERVO_ENABLE_PIN, gpioModePushPull, 0);

    /*
     * Configure GPIOs for the trigger inputs.  The port pins must be
     * configured for input, and connected to the external interrupt (EXTI)
     * facility.  At this stage, the interrupts are not enabled, this is
     * done later by calling ExtIntInit().
     */
    GPIO_PinModeSet (TRIG_POS_1_PORT, TRIG_POS_1_PIN, gpioModeInputPull, 1);
    GPIO_IntConfig  (TRIG_POS_1_PORT, TRIG_POS_1_PIN, false, false, false);

    GPIO_PinModeSet (TRIG_POS_2_PORT, TRIG_POS_2_PIN, gpioModeInputPull, 1);
    GPIO_IntConfig  (TRIG_POS_2_PORT, TRIG_POS_2_PIN, false, false, false);

    /* Create inactivity timer */
    l_thTimeout = sTimerCreate (ServoKeyTimeout);

    /* Enables the flash controller for writing. */
    MSC_Init();

    /* Initialize the eeprom emulator using 3 pages. */
    if ( !EE_Init(3) )
    {
	/* If the initialization fails we have to take some measure
	 * to obtain a valid set of pages. In this example we simply
	 * format the pages
	 */
	EE_Format(3);
    }

    /* Declare variables (virtual addresses) */
    EE_DeclareVariable(&magic);
    EE_DeclareVariable(&pos1);
    EE_DeclareVariable(&pos2);
    EE_DeclareVariable(&speed);
    EE_DeclareVariable(&chksum);

    /* Get servo end-points from flash */
    if (ReadServoParms())
    {
	l_ServoDataValid = true;
	l_ServoPos = l_ServoPos_1;
	l_ServoMode = SERVO_MODE_OPERATIONAL;
    }

    /*
     * We use timer 1 for the 50Hz time base (servo requires PWM pulse every
     * 20ms) and timer 2 for the pulse generation.  This is, timer 2 run in
     * one-shot mode and is triggered (reloaded and started) by timer 1.
     * CC0 (capture/compare channel 0) of timer 2 is routed to PC8.
     */
    /* Enable clock for GPIO module should already be done) */
    CMU_ClockEnable(cmuClock_GPIO, true);

    /* Enable clock for TIMER1 module */
    CMU_ClockEnable(cmuClock_TIMER1, true);

    /* Enable clock for the Peripheral Reflex System */
    CMU_ClockEnable(cmuClock_PRS, true);

    /* Enable clock for TIMER2 module */
    CMU_ClockEnable(cmuClock_TIMER2, true);

    /* Reset TIMER1, set default values for registers */
    TIMER_Reset(TIMER1);

    /* Select timer parameters */
    static const TIMER_Init_TypeDef timer1Init =
    {
	.enable     = false,			// do not start yet
	.debugRun   = true,
	.prescale   = timerPrescale16,		// 32Mhz / 16 = 2Mhz
	.clkSel     = timerClkSelHFPerClk,
	.fallAction = timerInputActionNone,
	.riseAction = timerInputActionNone,
	.mode       = timerModeUp,
	.dmaClrAct  = false,
	.quadModeX4 = false,
	.oneShot    = false,
	.sync       = false,
    };

    /* Initialize timer */
    TIMER_Init(TIMER1, &timer1Init);

    /* Set top value for the up-counter (50Hz, i.e. 20ms) */
    TIMER_TopSet(TIMER1, 2000000 / 50);

    /*
     * Build a connection from timer 1 overflow to timer 2 via the Peripheral
     * Reflex System (PRS) for triggering timer 2.
     */
    PRS_SourceSignalSet(0, PRS_CH_CTRL_SOURCESEL_TIMER1,
			   PRS_CH_CTRL_SIGSEL_TIMER1OF, prsEdgePos);

    /*
     * Timer 2 is used to generate a pulse on port C pin 8.
     */

    /* Enable clock for TIMER2 module */
    CMU_ClockEnable(cmuClock_TIMER2, true);

    /* Reset TIMER2, set default values for registers */
    TIMER_Reset(TIMER2);

    /*
     * Select CC0 channel parameters
     *
     * CC0 is only used to route channel 0 of the Peripheral Reflex System
     * (PRS) to the start/stop/reload logic of the timer. See Reference Manual,
     * figure "TIMER Block Overview" which shows a connection from CC0 to the
     * Counter Control block.
     */
    static const TIMER_InitCC_TypeDef timer2_CC0Init =
    {
	.eventCtrl  = timerEventEveryEdge,	// not used
	.edge       = timerEdgeBoth,		// pass both edges to control block
	.prsSel     = timerPRSSELCh0,		// PRS channel 0 is used
	.cufoa      = timerOutputActionNone,	// not used
	.cofoa      = timerOutputActionNone,	// not used
	.cmoa       = timerOutputActionNone,	// not used
	.mode       = timerCCModeOff,		// no capture or compare
	.filter     = false,			// not used
	.prsInput   = true,			// input from PRS channel
	.coist      = false,			// not used
	.outInvert  = false,			// not used
    };

    /* Configure CC channel 0 */
    TIMER_InitCC(TIMER2, 0, &timer2_CC0Init);

    /*
     * CC1 generates the output pulse for the servo via GPIO pin PC9.  We
     * use a 16MHz clock to be able to select a pulse width between 500us
     * and 2700us (max. 4000us) for the servo signal.
     */
    static const TIMER_InitCC_TypeDef timer2_CC1Init =
    {
	.eventCtrl  = timerEventEveryEdge,	// not used
	.edge       = timerEdgeBoth,		// pass both edges to control block
	.prsSel     = timerPRSSELCh0,		// not used
	.cufoa      = timerOutputActionNone,	// N/A for PWM mode
	.cofoa      = timerOutputActionNone,	// N/A for PWM mode
	.cmoa       = timerOutputActionNone,	// N/A for PWM mode
	.mode       = timerCCModePWM,		// start with high, switch to low
	.filter     = false,			// N/A for output modes
	.prsInput   = false,			// not used
	.coist      = false,			// N/A for PWM mode
	.outInvert  = false,			// no output pin inversion
    };

    /* Configure CC channel 1 */
    TIMER_InitCC(TIMER2, 1, &timer2_CC1Init);

    /* Set CC1 location pin PC9 as output */
    GPIO_PinModeSet(gpioPortC, 9, gpioModePushPull, 0);

    /* Route CC1 to location 2 and enable pin */
    TIMER2->ROUTE |= (TIMER_ROUTE_CC1PEN | TIMER_ROUTE_LOCATION_LOC2);

    /* Set Top Value - max. pulse width is 4ms based on a 16MHz clock */
    TIMER_TopSet(TIMER2, 16000 * 4);	// [kHz] * [ms]

    /* Generate a PWM signal that positions the servo in the middle */
    TIMER_CompareSet(TIMER2, 1, l_ServoPos);
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

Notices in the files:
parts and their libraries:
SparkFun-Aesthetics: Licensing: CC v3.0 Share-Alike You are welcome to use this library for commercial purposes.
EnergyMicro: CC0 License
